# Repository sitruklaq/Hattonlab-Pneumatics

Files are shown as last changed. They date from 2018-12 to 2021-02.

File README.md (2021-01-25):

# 1. Overview
This system is designed to control multi-channel pneumatic smart surfaces using only small amounts of air. The pneumatic system consists of 8 independent pneumatic channels that can access positive, negative, and neutral (exhaust) states. For a smaller, portable setup, please refer to this respository: https://github.com/sitruklaq/Mini-Pneumatics

image of setup

topView backView

## 1.1 Table of Contents
* [1\. Overview](#1-overview)
  * [1\.1 Table of Contents](#11-table-of-contents)
* [2\. Components &amp; Pneumatic Logic](#2-components--pneumatic-logic)
* [3\. Instrument Control](#3-instrument-control)
  * [3\.1 Serial Command List](#31-serial-command-list)
    * [3\.1\.1 Valve Control](#311-valve-control)
    * [3\.1\.2 Reservoir Setpoints](#312-reservoir-setpoints)
    * [3\.1\.3 Pressure Readings](#313-pressure-readings)
* [4\. Visual Control App](#4-visual-control-app)
* [5\. Setpoint Pressure Control](#5-setpoint-pressure-control)
* [6\. Electrical Circuitry](#6-electrical-circuitry)
  * [6\.1 Electrical Components](#61-electrical-components)
  * [6\.2 PCBs](#62-pcbs)
    * [6\.2\.2 Input Valve PCB](#622-input-valve-pcb)
    * [6\.2\.3 Output Valve PCB](#623-output-valve-pcb)
    * [6\.2\.4 2 Sensor Board](#624-2-sensor-board)
[TOC]
# 2. Components & Pneumatic Logic

The instrument is designed to provide 3 pressure 'input' states: positive (+∆P), negative, (-∆P), and neutral (0∆P). Postive and negative pressures are generated through pneumatic pumps and held in reservoirs. The pressure for each reservoir is defined by the user and monitored through in-line pressure sensors. Pneumatic valves can be toggled to open and enter a common pressure line which can be accessed by independent valves that lead to channels (N=8). 

The valves are rated for +-100kPa while the pumps are generally able to reach ~+-60kPa. Valve response time is <5ms.

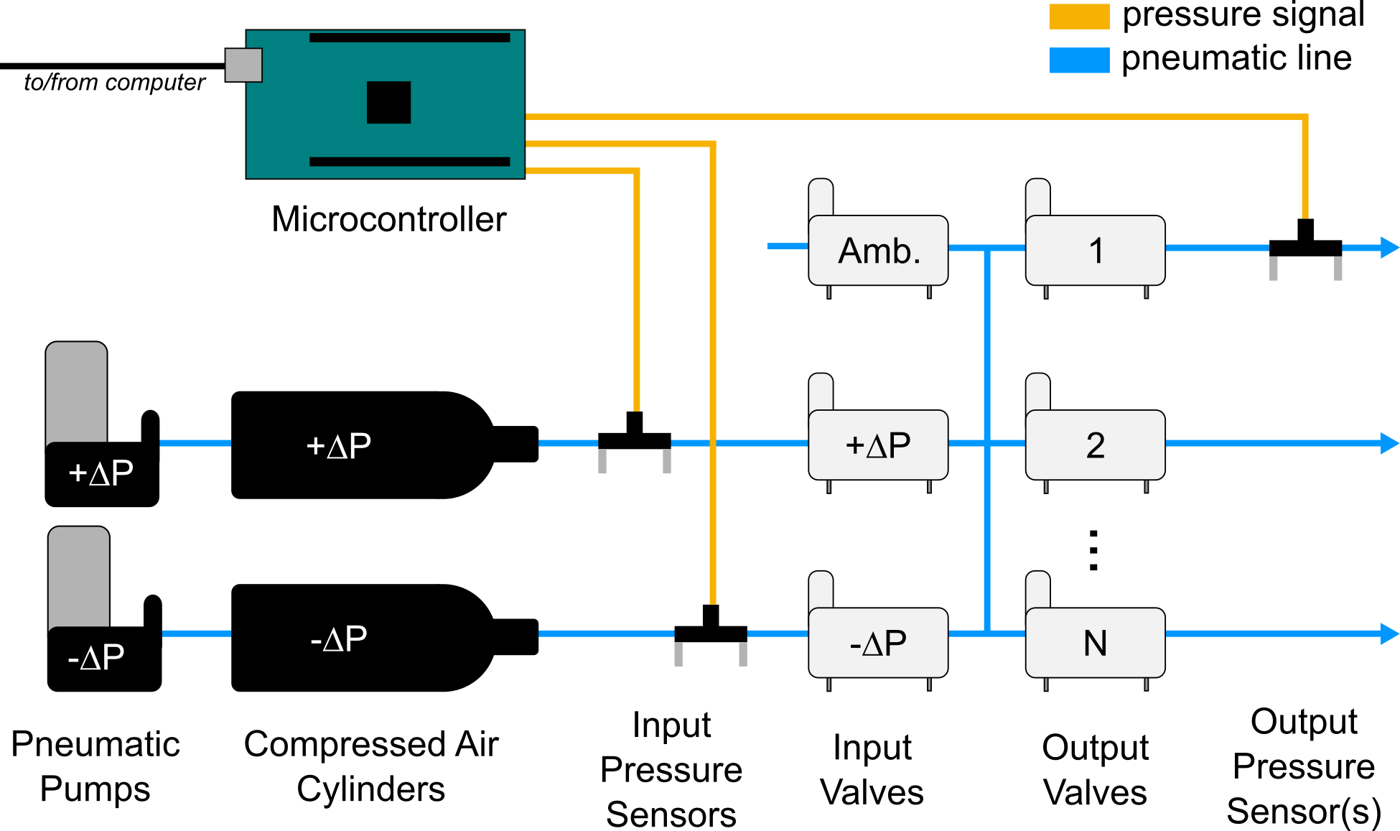
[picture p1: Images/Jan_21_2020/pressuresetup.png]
image of logic


# 3. Instrument Control

An Arduino microncontroller is responsible for opening and closing the pneumatic valves in addition to regulating pressure setpoints of the reservoirs. 

This instrument is controlled through a Serial Connection to a computer. 

Communication to the microcontroller is accomplished through serial communication. Commands for valve control, setpoint, and pressure value requests are available in the X section.

A MATLAB GUI app uses these commands to visually control the pneumatics.

screenshot to be added later.

## 3.1 Serial Command List

The Arduino is listening for serial commands in the following structure ‘< command, optional modifier, optional modifier>’.

### 3.1.1 Valve Control

| Command Syntax | Description                                                  | Example                                 |
| :------------: | ------------------------------------------------------------ | --------------------------------------- |
|     **VO**     | **VALVE OUTPUT** Changes the state of a single output valve. <command, valve # (0-7), valve state (0-closed 1-open)> | <VO, 4, 1> opens the fifth output valve |
|     **VI**     | **VALVE INPUT**Changes the state of a single input valve. <command, valve # (0-7), valve state (0-off 1-on)> | <VO, 4, 1> opens the fifth output valve |
|    **AIV**     | **ALL INPUT VALVES** Changes the state of all input valves <command, 0/1> | <AIV,1> opens all input valves          |
|    **AOV**     | **ALL OUTPUT VALVES** Changes the state of all outpu valves <command, 0/1> | <AOV, 0> turns off all output valves    |

### 3.1.2 Reservoir Setpoints

| Command Syntax | Description                                                  | Example    |
| :------------: | ------------------------------------------------------------ | ---------- |
|    **PSP**     | Changes setpoint of positive pressure reservoir              | <PSP, 15>  |
|    **NSP**     | Changes setpoint of negative pressure reservoir              | <NSP, -15> |
|    **PVN**     | **PRESSURE VALUE NEGATIVE** prints the pressure value of the negative pressure reservoir | <PVN>      |
|    **PVO**     | **PRESSURE VALUE OUTPUT** prints the pressure value of an output pressure channel | <PVO, 3>   |
|    **PVP**     | **PRESSURE VALUE POSITIVE** prints the pressure value of the positive pressure reservoir | <PVP>      |

### 3.1.3 Pressure Readings

| Command Syntax | Description                                                  | Example  |
| :------------: | ------------------------------------------------------------ | :------: |
|      PVP       | **PRESSURE VALUE POSITIVE** prints the pressure value of the positive pressure reservoir |  <PVP>   |
|      PVN       | **PRESSURE VALUE NEGATIVE** prints the pressure value of the negative pressure reservoir |  <PVN>   |
|      PVO       | **PRESSURE VALUE OUTPUT** prints the pressure value of an output pressure channel | <PVO, 3> |

# 4. Visual Control App

A visual control app was designed using Matlab App Designer. The app is basic in functionality but is able to control valves through sending serial commands. 

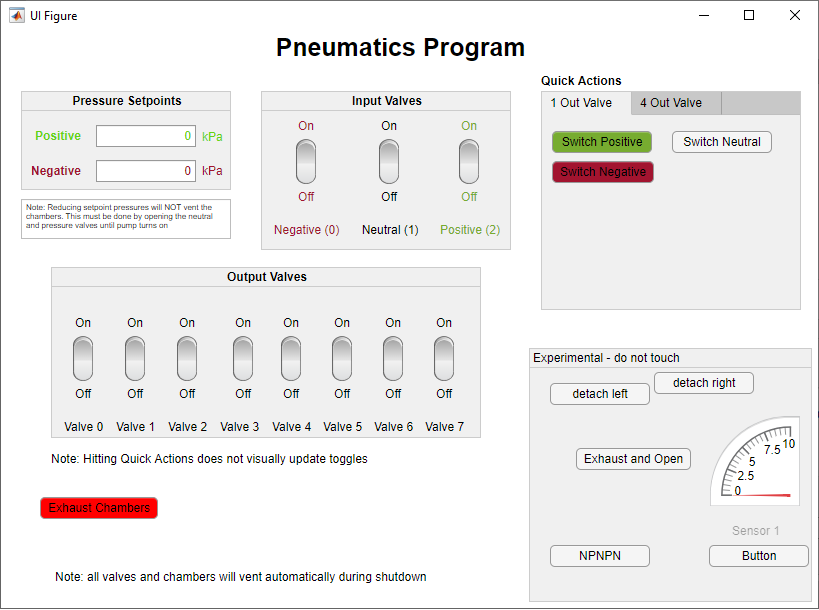
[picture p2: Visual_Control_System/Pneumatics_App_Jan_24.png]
VCA


# 5. Setpoint Pressure Control

Reservoir pressure is controlled by simple state monitoring. The pressure sensors monitor the pressure and the pump is turned on if the pressure drops below the Setpoint (with a small threshold).

# 6. Electrical Circuitry

## 6.1 Electrical Components

Power is supplied by an off board 12V 5A brick-style switching power supply. The 12V power is then split and one side is stepped down to 5V. The valves run on the 5V rail and are toggled through npn transistors powered by an Arduino.

**12V**

- Pumps
- Motor Controller

**5V**

- Valves

**5V (Computer-> Arduino)**

- pressure sensors
- transistors
- leds

## 6.2 PCBs

### 6.2.2 Input Valve PCB

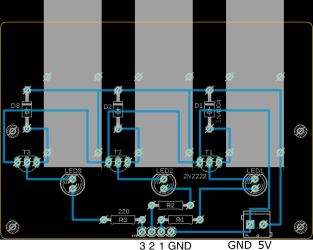
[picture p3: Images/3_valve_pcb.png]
3 valve pcb


### 6.2.3 Output Valve PCB

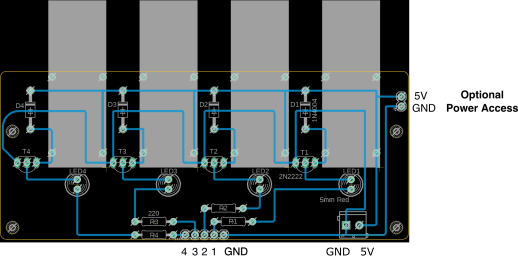
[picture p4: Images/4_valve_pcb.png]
4 valve pcb


### 6.2.4 2 Sensor Board

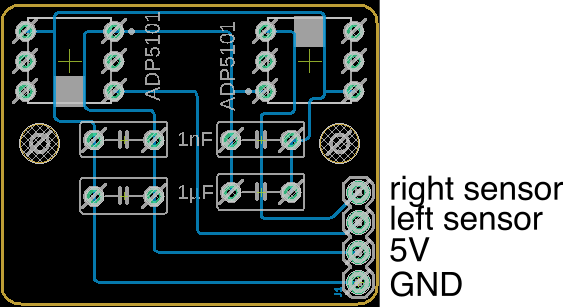
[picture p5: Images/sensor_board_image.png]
sensor board


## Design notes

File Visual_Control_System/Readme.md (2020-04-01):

# Things to Add

- [ ] Add pump pressure value gauges
- [ ] add pump power gauge
- [ ] add fluctuate quick action
- [ ] mimic valve positions to real device
- [ ] real-time update of toggle switches if quick actions are pressed

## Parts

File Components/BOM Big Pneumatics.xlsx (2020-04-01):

Hattonlab Pneumatics BOM
 | Description | Quantity | Unit Cost | Total Cost | Part Number` | Supplier | Purchase Link | Notes
Power Generation | Power Supply 12V 6A switching | 1 |  |  |  | creatroninc | not available
 | Barrel Jack 2.1mm DC | 1 | $0.65 | $0.65 |  | creatroninc | https://www.creatroninc.com/product/1mm-dc-barrel-jack/?search_query=barrel+jack&results=22
 | Switch SPST Rocker | 1 | $1.25 | $1.25 | SWROC-121801 | creatroninc | https://www.creatroninc.com/product/spst-rocker-switch/?search_query=switch&results=298
 | Voltage Regulator DROK DC Car Power Supply Voltage Regulator Buck Converter 8A/100W 12A Max DC 5-40V to 1.2-36V Step Down Volt Convert Module | 1 | $11.99 | $11.99 |  | amazon.ca | https://www.amazon.ca/gp/product/B00C4QVTNU/ref=ppx_yo_dt_b_search_asin_title?ie=UTF8&psc=1
Electrical Control | Arduino Mega Microcontroller | 1 | $19.99 | $19.99 | Arduino 2560 | amazon.ca | https://www.amazon.ca/Elegoo-Board-ATmega2560-ATMEGA16U2-Arduino/dp/B01H4ZDYCE?s=hi
 | Motor Controller L298 DUAL MOTOR DRIVER - 2A | 1 | $14.00 | $14.00 | PROMR-025298 | creatroninc | https://www.creatroninc.com/product/l298-dual-motor-driver-2a/?search_query=motor+controller&results=46 | I don’t think this is necessary and it is definitely a power hog.. Don’t use in version 2
Pneumatics | Pneumatic Pumps Vacuum Pump 12V Mini Diaphragm Air Compressor with Silicone Tube | 2 | $27.95 | $55.90 |  | creatroninc | https://www.creatroninc.com/product/12v-vacuum-pump/?search_query=pump&results=8
 | Pneumatic Valves | 11 | $6.95USD EA (min 25) | 76.45 |  | Jameco | https://www.jameco.com/z/RLB204KP30B-Asco-Valve-and-Instrument-2-Way-Barbed-Solenoid-Air-Valve-Normally-Closed_2258401.html | cheaper if purchased in bulk
Valve Control | terminal block
 | diode 1N4001 50V 1A rectifier Diode | 11 | 0.105 (0.42 per 4) | $1.16 | DIREC-004001 | creatroninc | https://www.creatroninc.com/product/1n4001-50v-1a-rectifier-diode-4-pack/?search_query=diode&results=75
 | transistor SS8050 - NPN BJT (25V 1.5A) | 11 | 0.6 | $6.60 | TRANQ-008050 | creatroninc | https://www.creatroninc.com/product/ss8050-npn-bjt-25v-15a/?search_query=transistor&results=146
 | resistor | 11 | ~0 | $0.00 |  | find a resistor pack around
 | led RED 5mm 2.2V 8mA | 11 | 0.1 (2.00 per 20) | $1.10 | LEDGE-000320 | creatroninc | https://www.creatroninc.com/product/3mm-led-red-20-pack/?search_query=led&results=464
sensor bank | pressure sensor Panasonic +-100kPa DIP mount | 7 | 60 | $420.00 | 769-ADP5101 | mouser.ca | https://www.mouser.ca/ProductDetail/Panasonic/ADP5101
 | capacitor
 | terminal block
PCBS | dual or one sided PCB | ~2 | $24 per 25 | 192% |  | bantamtools.com | https://www.bantamtools.com/miscellaneous/printed-circuit-board-blanks
Housing | Acrylic Sheet |  |  |  |  | mcmastercarr
 | standoffs |  |  |  |  | mcmastercarr
Assorted | tubing
 | luer connectors
 | check valves | 2 | 6.12CAD (per10) | 6.12 | Cole-Parmer AO-30505-92 | amazon.ca | https://www.amazon.ca/Cole-Parmer-One-way-silicone-diaphragm-female-male/dp/B003NVAG8O?s=gateway
 | standoffs and screws 250Pcs M3 Male to Female Hex Column Standoff Spacer Pillars Screws Nuts Assortment Kit with Storage Box (M3) | 1 pack | 18.69 |  |  | amazon.ca | https://www.amazon.ca/250Pcs-Standoff-Pillars-Assortment-Storage/dp/B071RXSMW6?s=gateway
 | electrical wiring

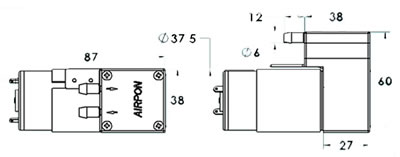
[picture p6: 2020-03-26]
Components/53cd24320585a-d2028bb.jpg

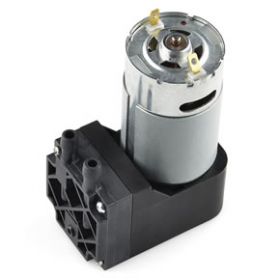
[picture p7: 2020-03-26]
Components/ROB-10398__00509.jpg

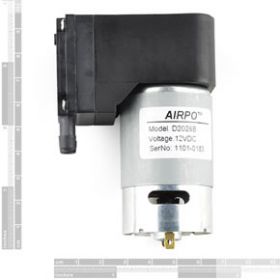
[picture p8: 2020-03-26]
Components/ROB-10398A__23939.jpg

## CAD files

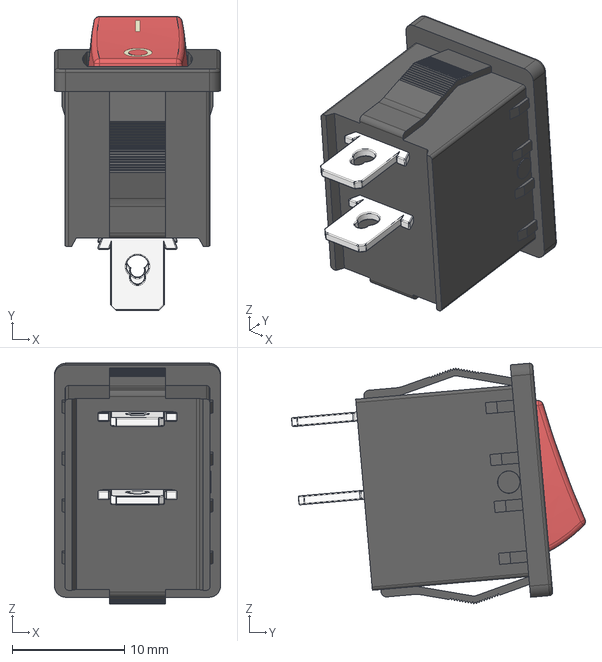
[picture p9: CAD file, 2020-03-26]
CAD FILES/rocker-switch-14/Rocker Assembly.stp
14.8 x 26.2 x 21.5 mm
Rocker SW samo taster horizont
Rocker SW samo telo

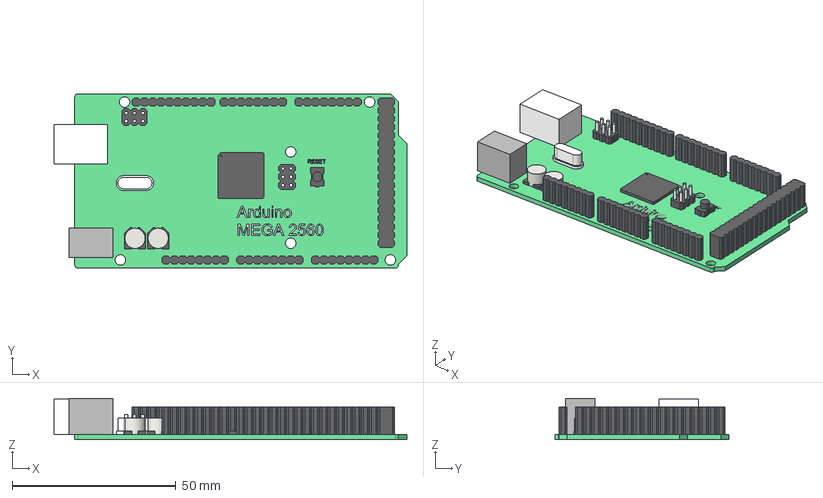
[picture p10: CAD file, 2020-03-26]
CAD FILES/arduino-mega-2560/ArduinoMEGA2560.stp
107.9 x 53.3 x 12.6 mm

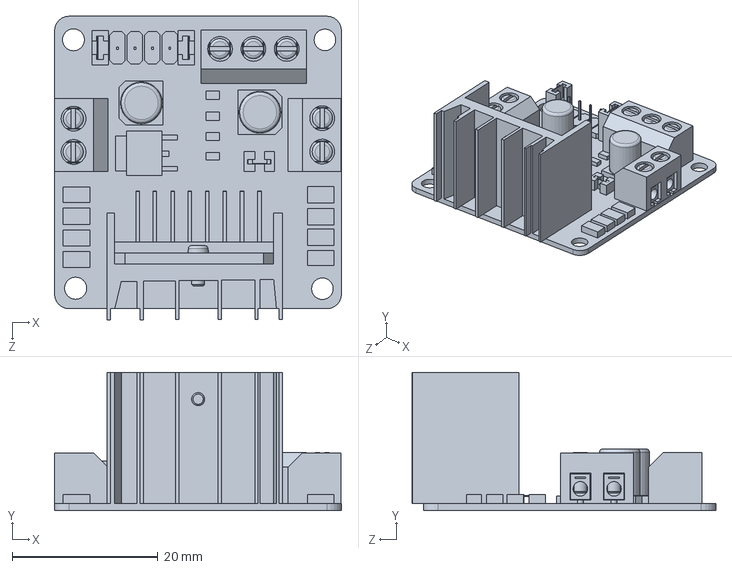
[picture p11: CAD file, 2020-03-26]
CAD FILES/l298n-driver-1/L298N Driver/L298N.SLDPRT
39.4 x 19.0 x 41.7 mm

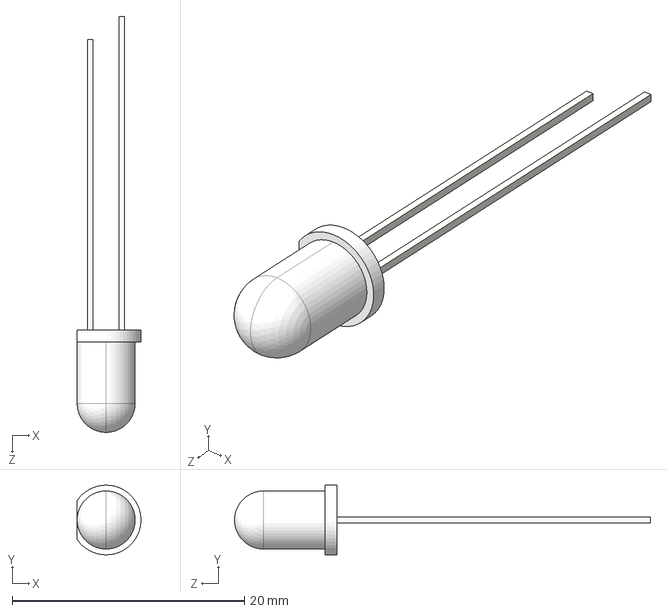
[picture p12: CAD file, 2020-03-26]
CAD FILES/led-5mm-1/LED 5mm.STEP
5.49 x 6.00 x 35.8 mm

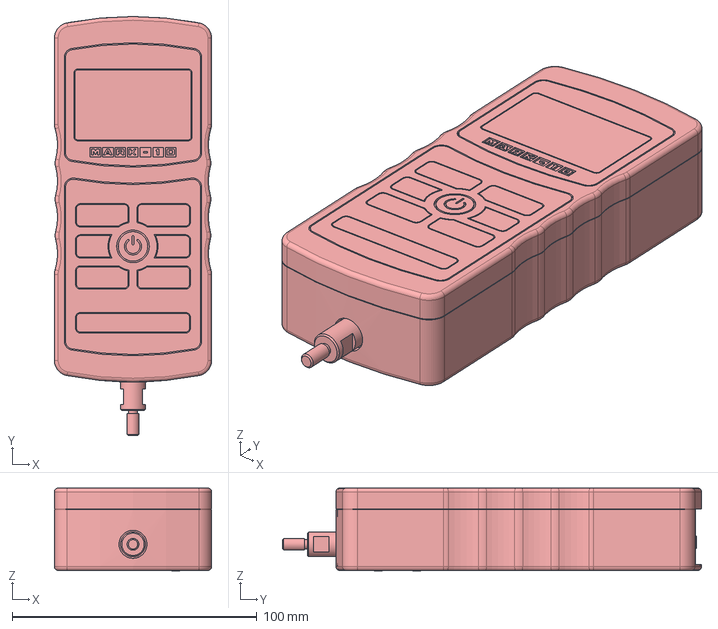
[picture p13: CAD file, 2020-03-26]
CAD FILES/M4/M4.stp
64.3 x 171.2 x 33.8 mm

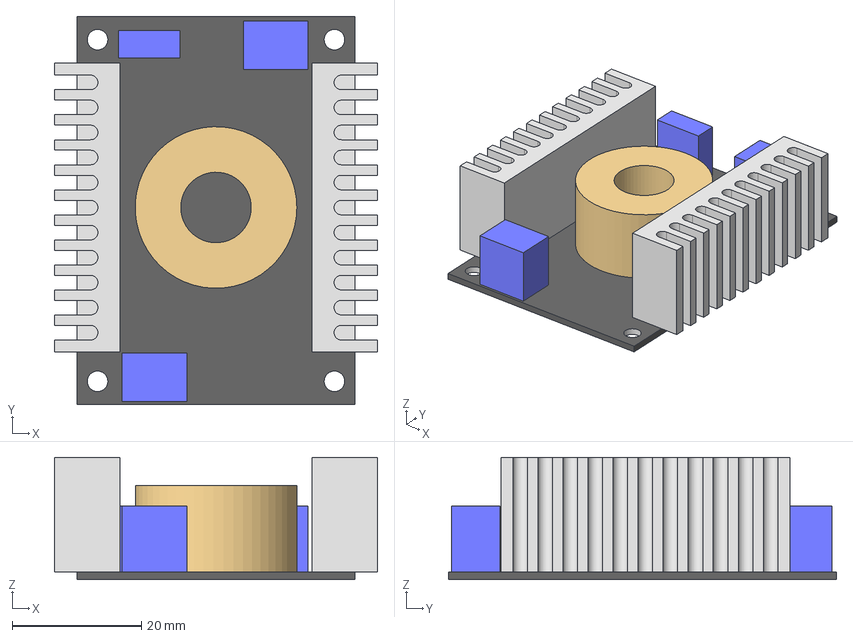
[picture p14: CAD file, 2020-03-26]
CAD FILES/Voltage Converter/DROK_090483.stp
50.0 x 60.0 x 18.9 mm

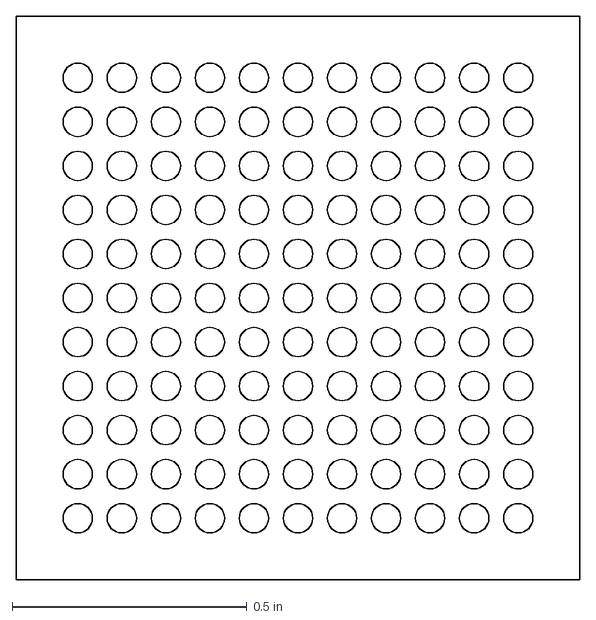
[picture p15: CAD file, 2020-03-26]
CAD FILES/holes.dxf
1.20 x 1.20 in

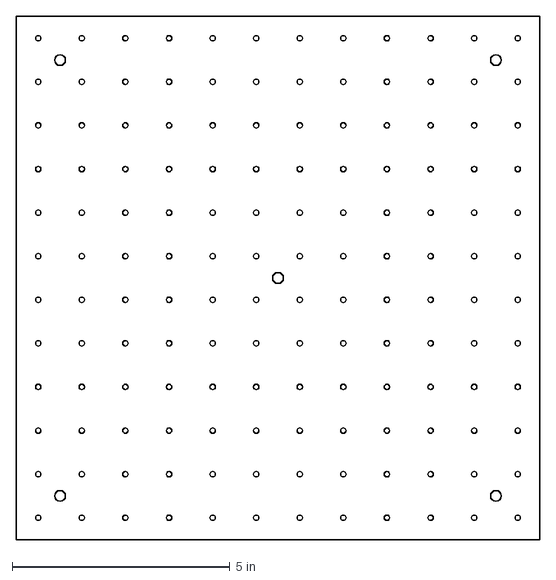
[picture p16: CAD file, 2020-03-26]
CAD FILES/top plate.dxf
12.0 x 12.0 in

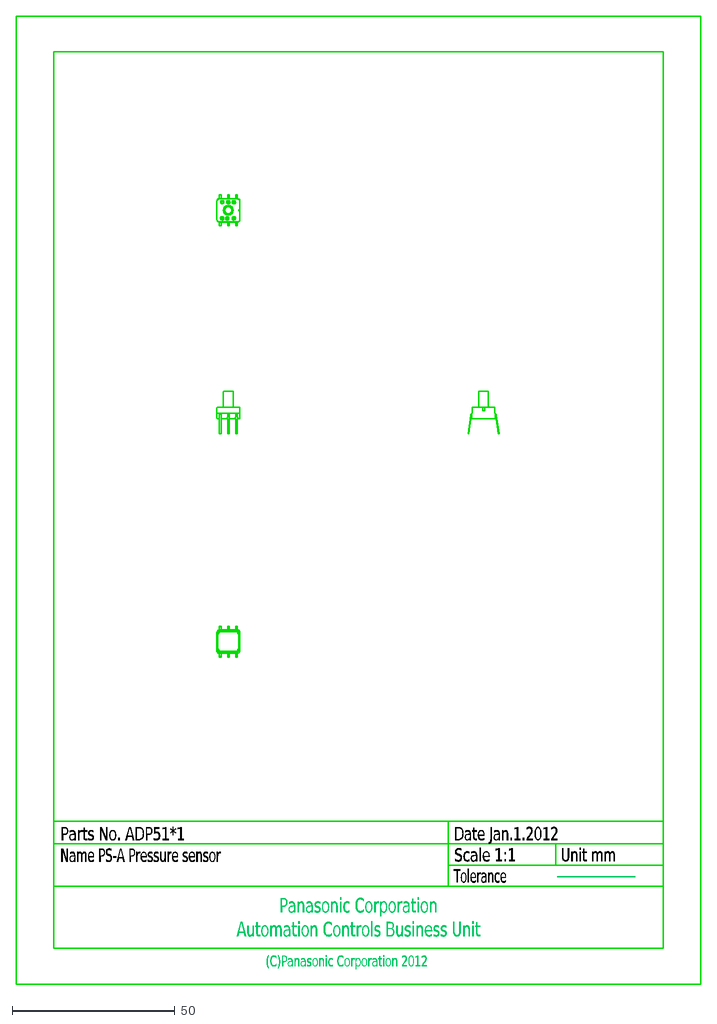
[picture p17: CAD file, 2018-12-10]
CAD FILES/adp5101.dxf
Parts No. ADP51*1
Name PS-A Pressure sensor
Scale 1:1
Unit mm
Tolerance
(C)Panasonic Corporation 2012
Panasonic Corporation Automation Controls Business Unit
Date Jan.1.2012

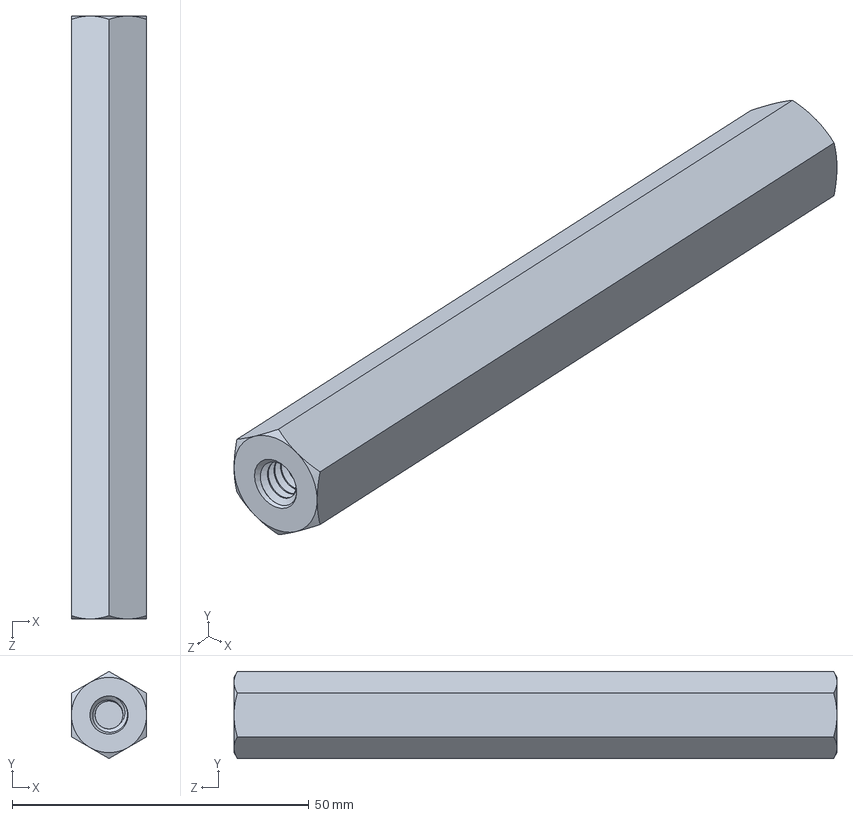
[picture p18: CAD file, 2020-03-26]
CAD FILES/91780A365_ALUM FEM THRDED HEX STANDOFF.SLDPRT
12.7 x 14.7 x 101.6 mm

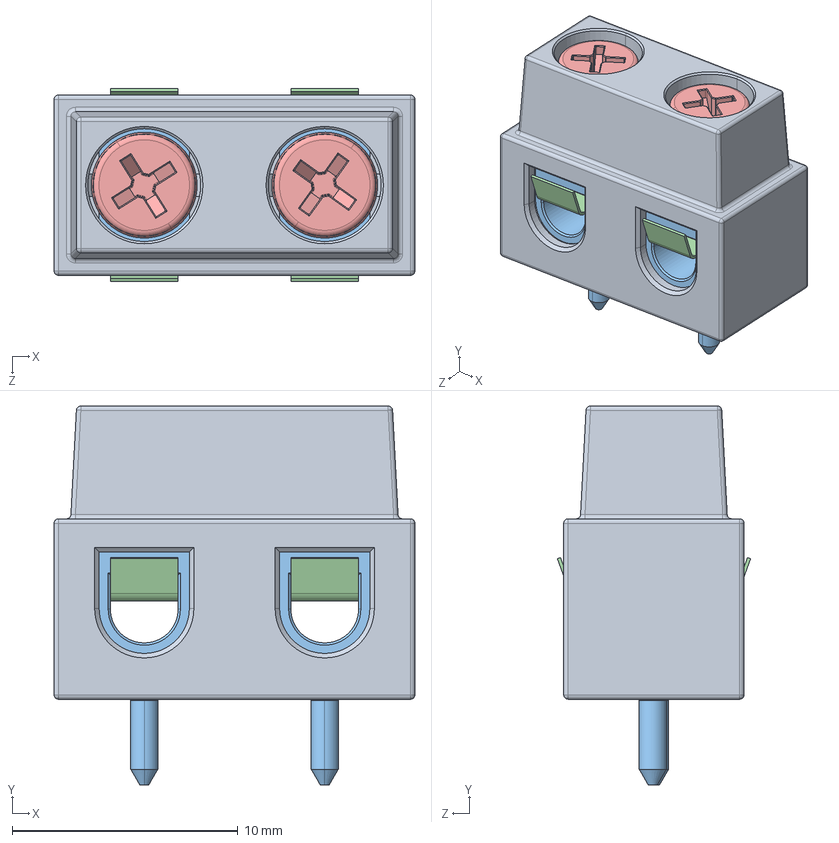
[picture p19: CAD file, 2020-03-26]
CAD FILES/screw-connection-terminal-1/Screw connection terminal.STEP
16.0 x 16.8 x 8.57 mm
terminal_S_case
wire insertion x 2
washer x 2
M2,5_0,35 x 2

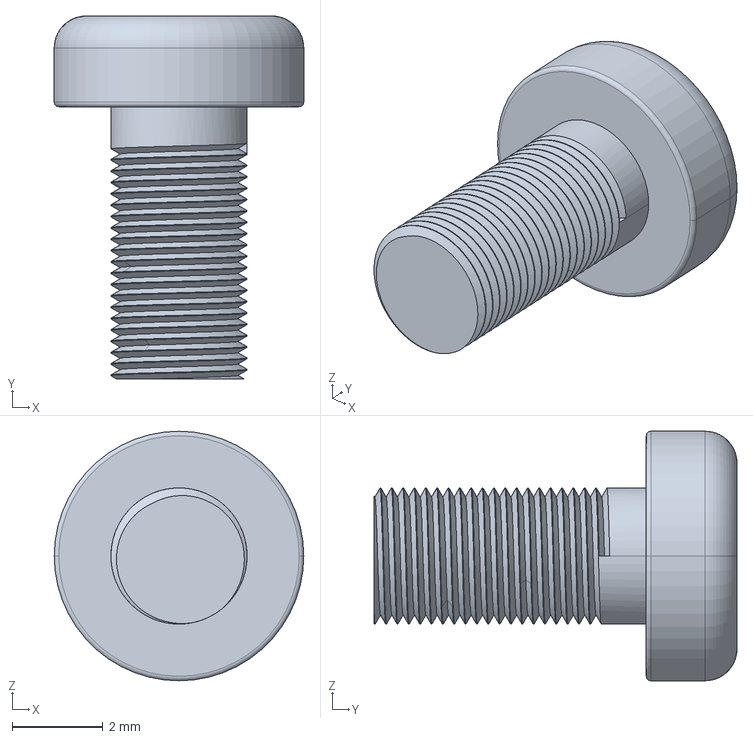
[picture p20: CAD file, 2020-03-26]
CAD FILES/screw-m3-x-0-5-length-6mm-pan-head-philips-drive-1/1220-1000-010-std-screw-m3x6.stp
5.50 x 8.00 x 5.50 mm

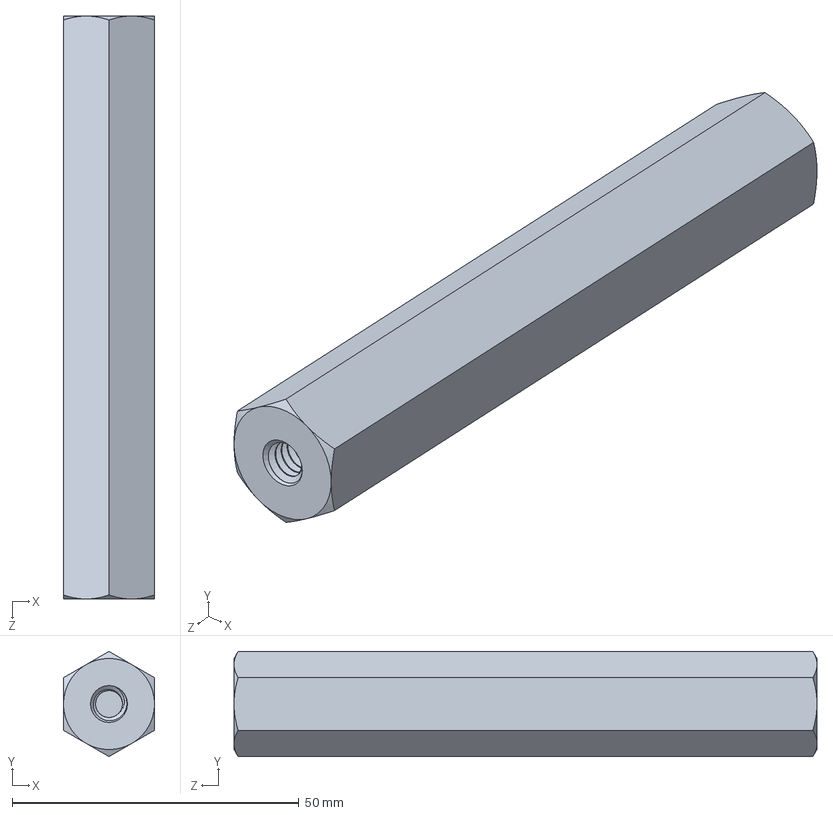
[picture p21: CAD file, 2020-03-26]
CAD FILES/91780A254_ALUM FEM THRDED HEX STANDOFF.SLDPRT
15.9 x 18.3 x 101.6 mm

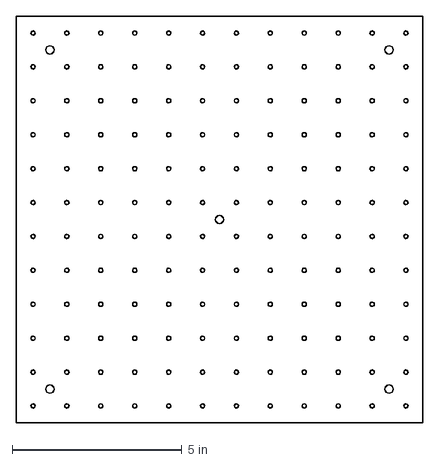
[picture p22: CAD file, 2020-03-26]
CAD FILES/screw-m3-x-0-5-length-6mm-pan-head-philips-drive-1/acrylic plates.dxf
12.0 x 12.0 in

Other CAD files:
CAD FILES/12v pump.f3d
CAD FILES/M4/M4.dwg
CAD FILES/M4/M4.igs
CAD FILES/Voltage Converter/DROK_090483.ipt
CAD FILES/air tank v1.f3d
CAD FILES/arduino-mega-2560/ArduinoMEGA2560.ipt
CAD FILES/arduino-mega-2560/ArduinoMega v1.f3d
CAD FILES/arduino-mega-2560/Arduino_MEGA2560.stl
CAD FILES/l298n-driver-1/L298N v1.f3d
CAD FILES/led-5mm-1/LED 5mm.IGS
CAD FILES/led-5mm-1/LED 5mm.SLDPRT
CAD FILES/led-5mm-1/LED 5mm.STL
CAD FILES/screw-m3-x-0-5-length-6mm-pan-head-philips-drive-1/1220-1000-010-std-screw-m3x6.igs

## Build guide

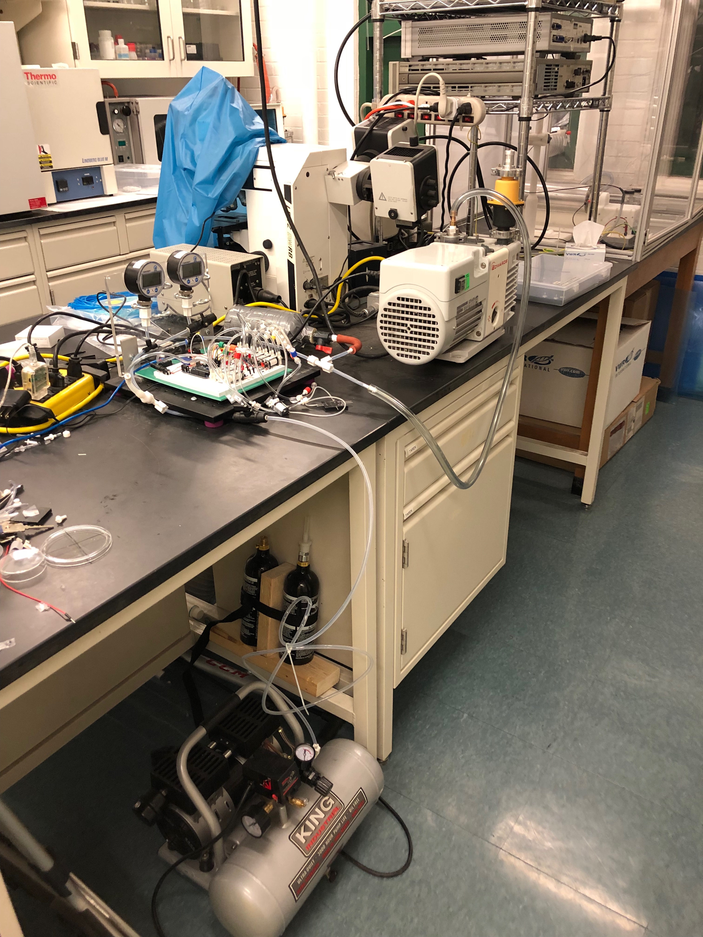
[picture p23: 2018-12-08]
Images/February 2018/Setup Feb 17 2018.jpg

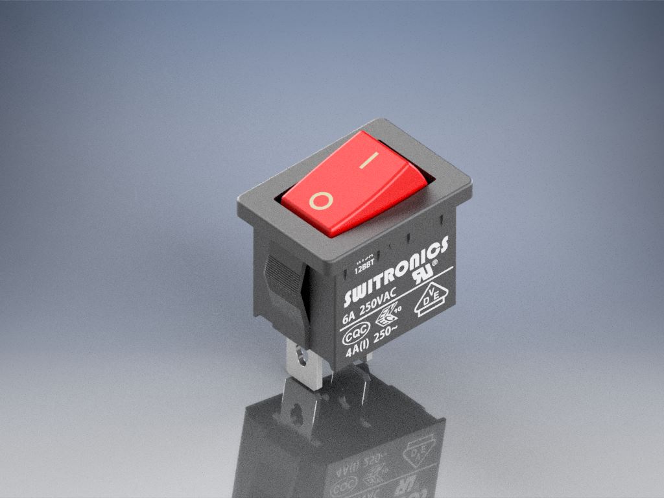
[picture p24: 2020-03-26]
CAD FILES/rocker-switch-14/Rocker Assembly.jpg

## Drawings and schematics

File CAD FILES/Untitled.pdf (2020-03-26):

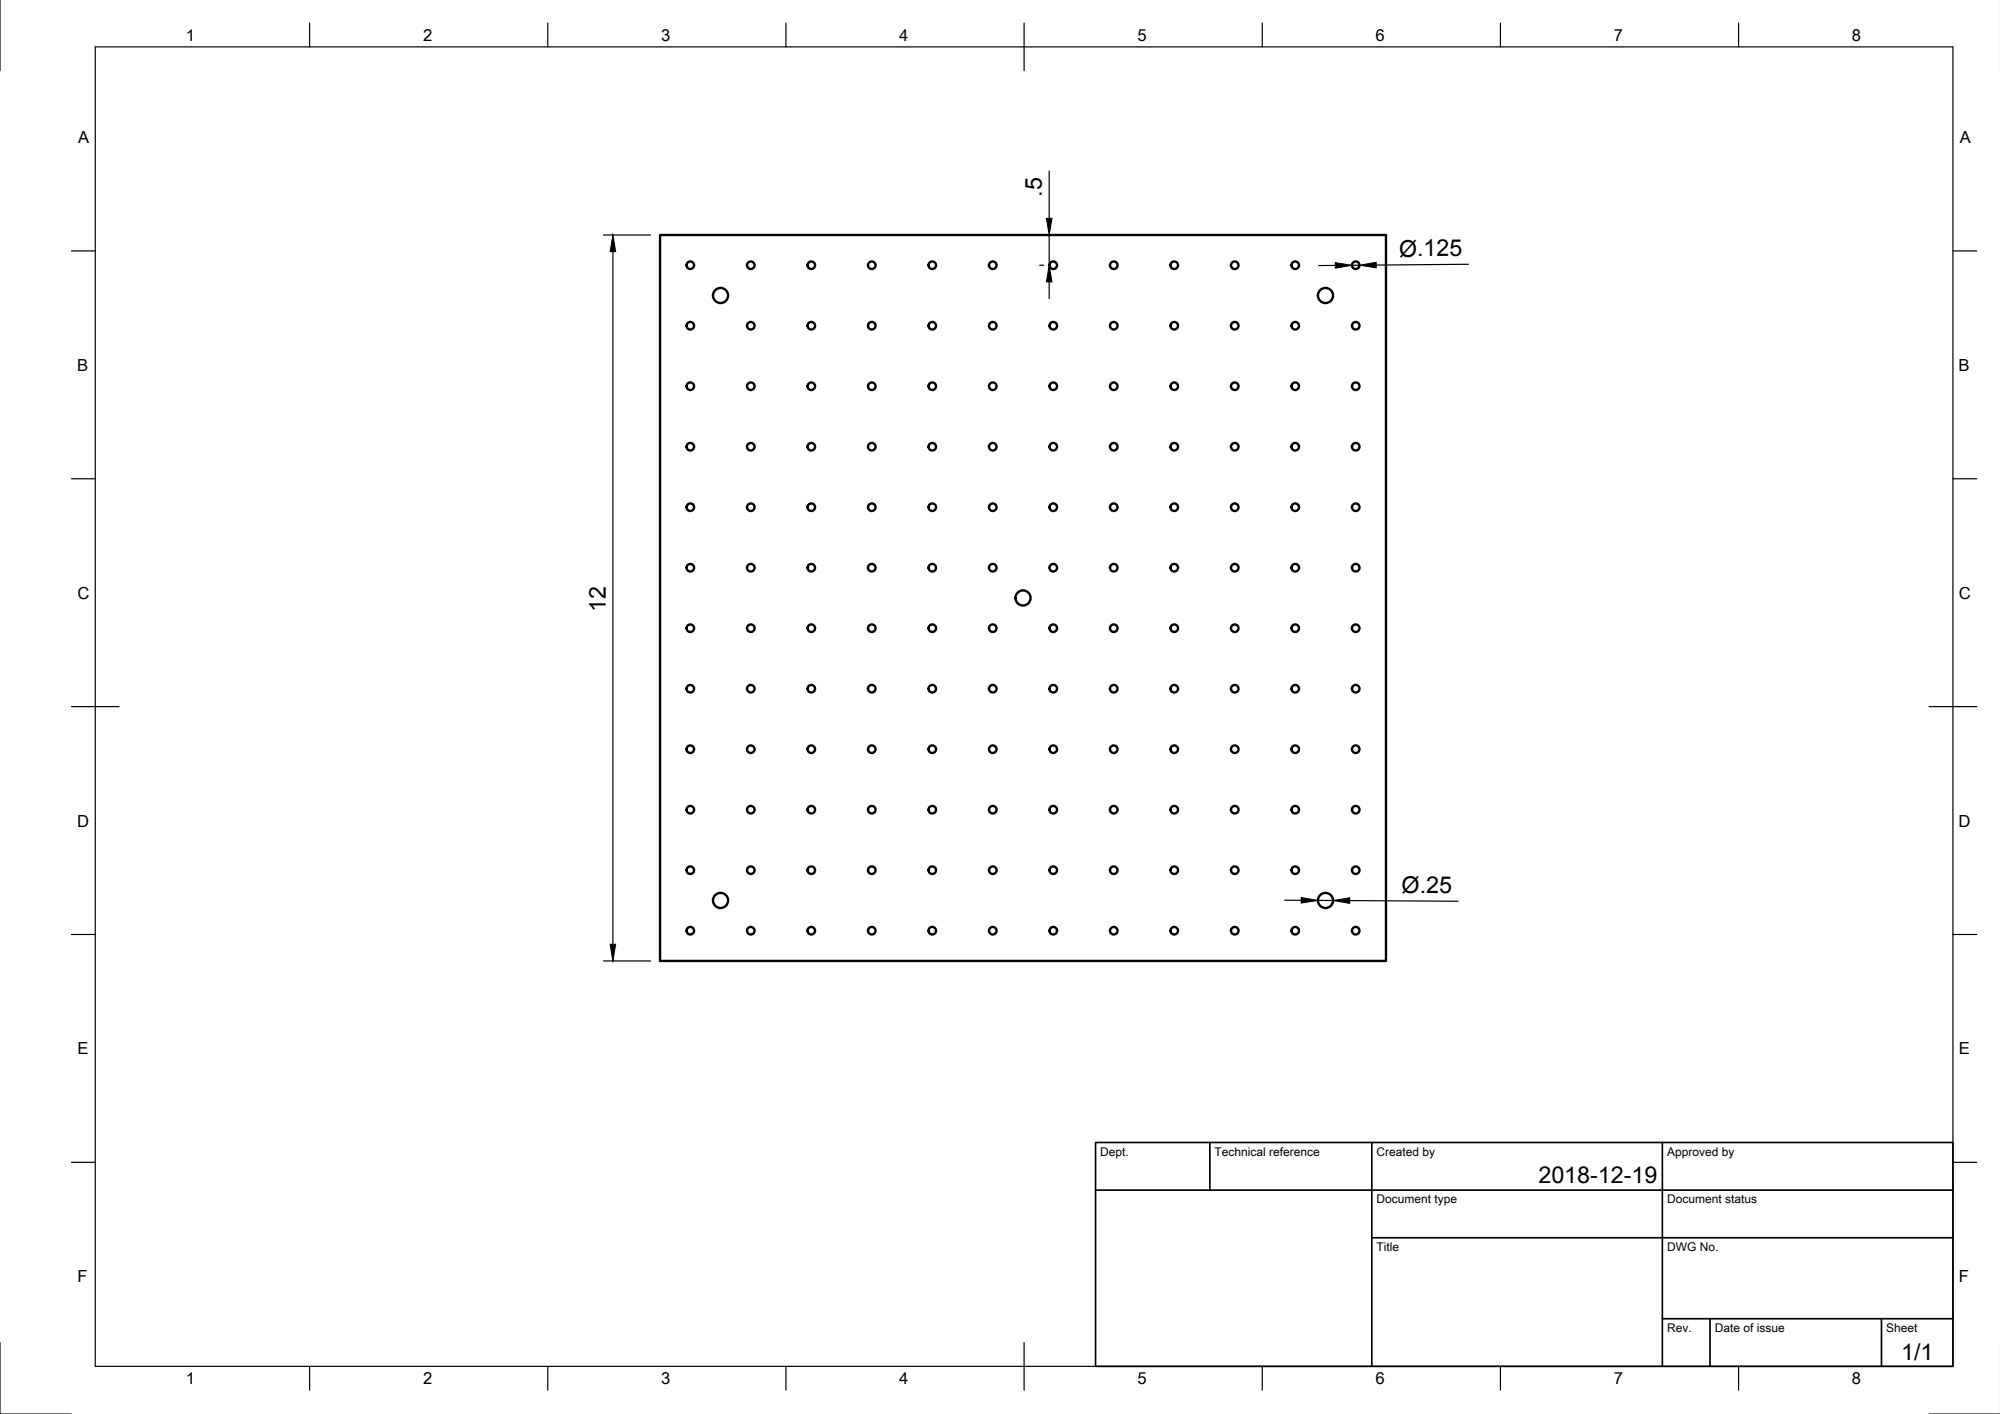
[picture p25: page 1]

Dept. | Technical reference | Created by 2018-12-19 | Approved by

Document type | Document status

Title | DWG No.

Rev. | Date of issue | Sheet 1/1

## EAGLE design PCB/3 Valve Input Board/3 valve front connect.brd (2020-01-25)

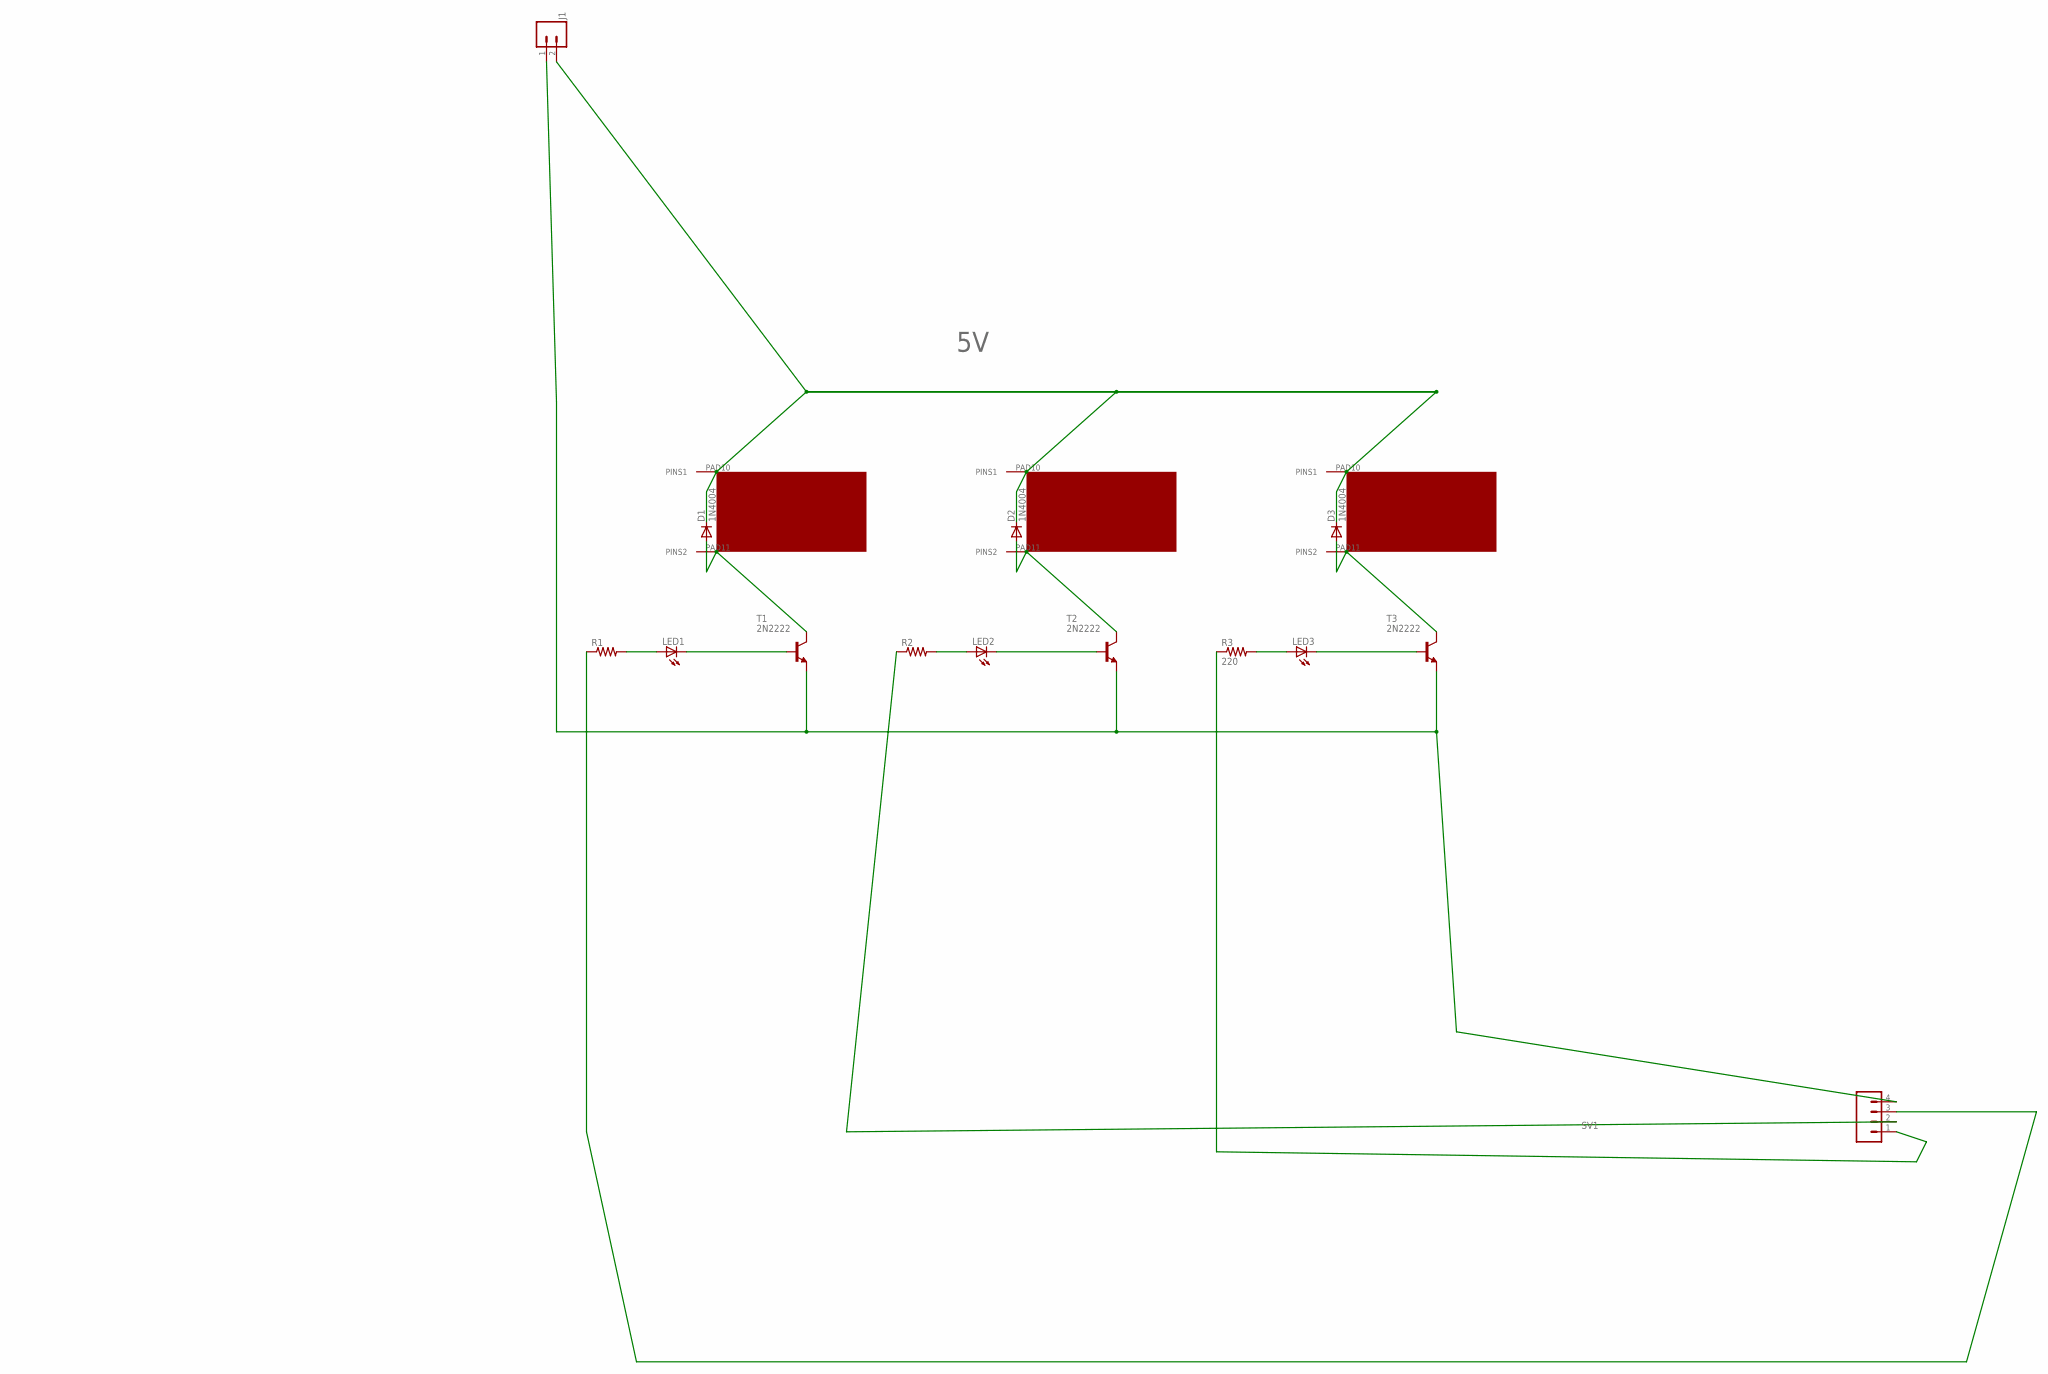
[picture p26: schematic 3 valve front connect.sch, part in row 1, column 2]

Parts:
D1, D2, D3: 1N4004; DO41-10
J1: CONN_023.5MM; SCREWTERMINAL-3.5MM-2
LED1, LED2, LED3: LED5MM
R1, R2: R-US_0207/10; 0207/10
R3: 220; 0207/10
SV1: CONN_04; 1X04
T1, T2, T3: 2N2222; TO92-EBC-OVAL
U$1, U$2: VALVE; VALVTEST2
VALVE3: VALVE; VALVTEST2

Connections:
5V: D1.C, D2.C, D3.C, J1.2, U$1.PAD10 (PINS1), U$2.PAD10 (PINS1), VALVE3.PAD10 (PINS1)
GND: J1.1, SV1.4, T1.E, T2.E, T3.E
unnamed: D1.A, T1.C, U$1.PAD11 (PINS2)
unnamed: LED1.K (C), T1.B
unnamed: LED1.A, R1.2
unnamed: D2.A, T2.C, U$2.PAD11 (PINS2)
unnamed: LED2.K (C), T2.B
unnamed: LED2.A, R2.2
unnamed: D3.A, T3.C, VALVE3.PAD11 (PINS2)
unnamed: LED3.K (C), T3.B
unnamed: LED3.A, R3.2
unnamed: R3.1, SV1.1
unnamed: R1.1, SV1.3
unnamed: R2.1, SV1.2

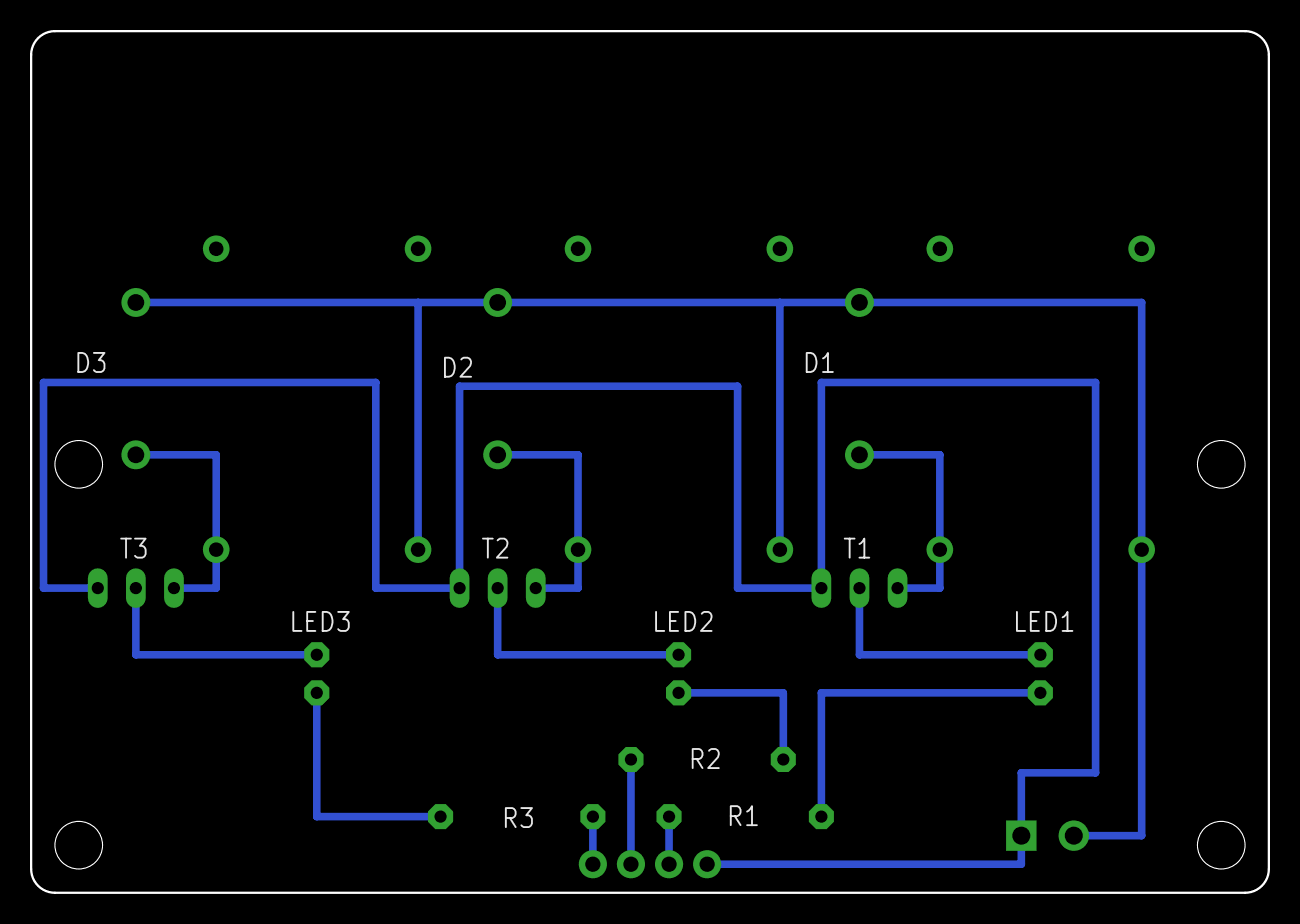
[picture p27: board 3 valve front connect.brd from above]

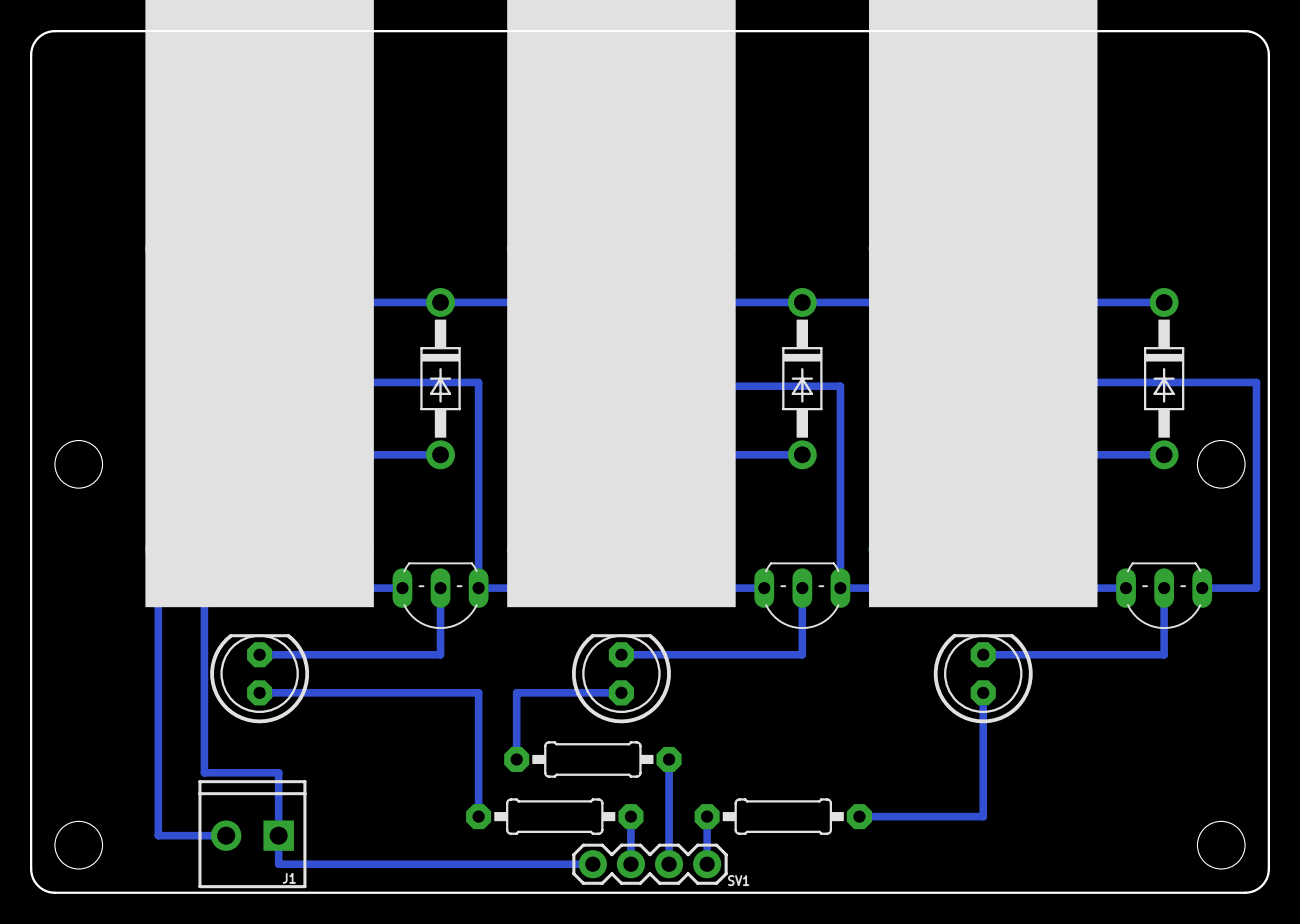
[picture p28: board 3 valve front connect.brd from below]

Board: 2 copper layers, 82.6 x 57.5 mm, 17 parts (17 on the bottom side), 14 nets.

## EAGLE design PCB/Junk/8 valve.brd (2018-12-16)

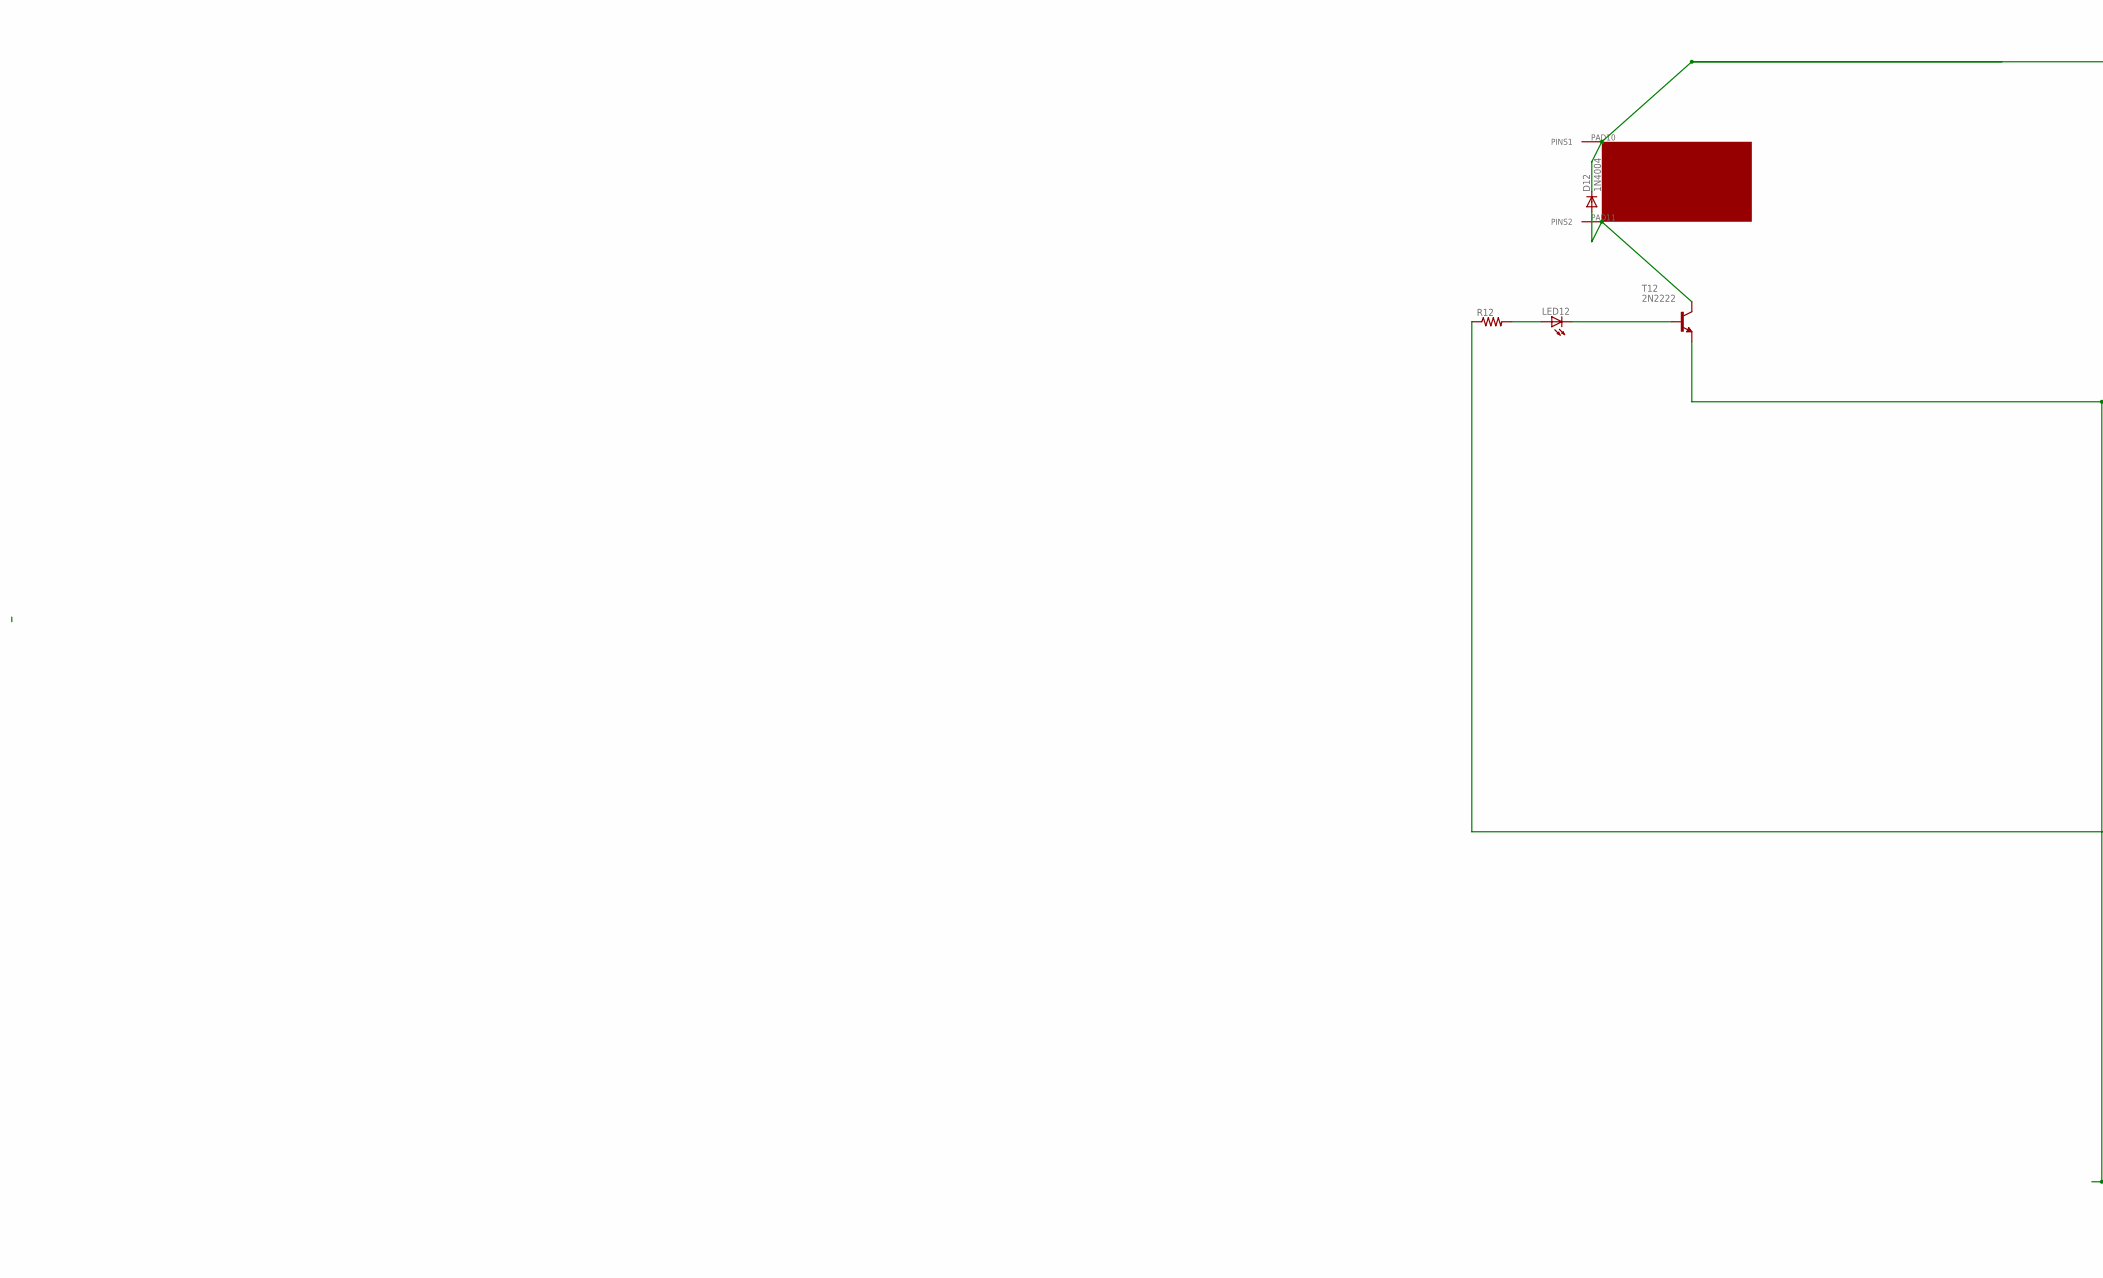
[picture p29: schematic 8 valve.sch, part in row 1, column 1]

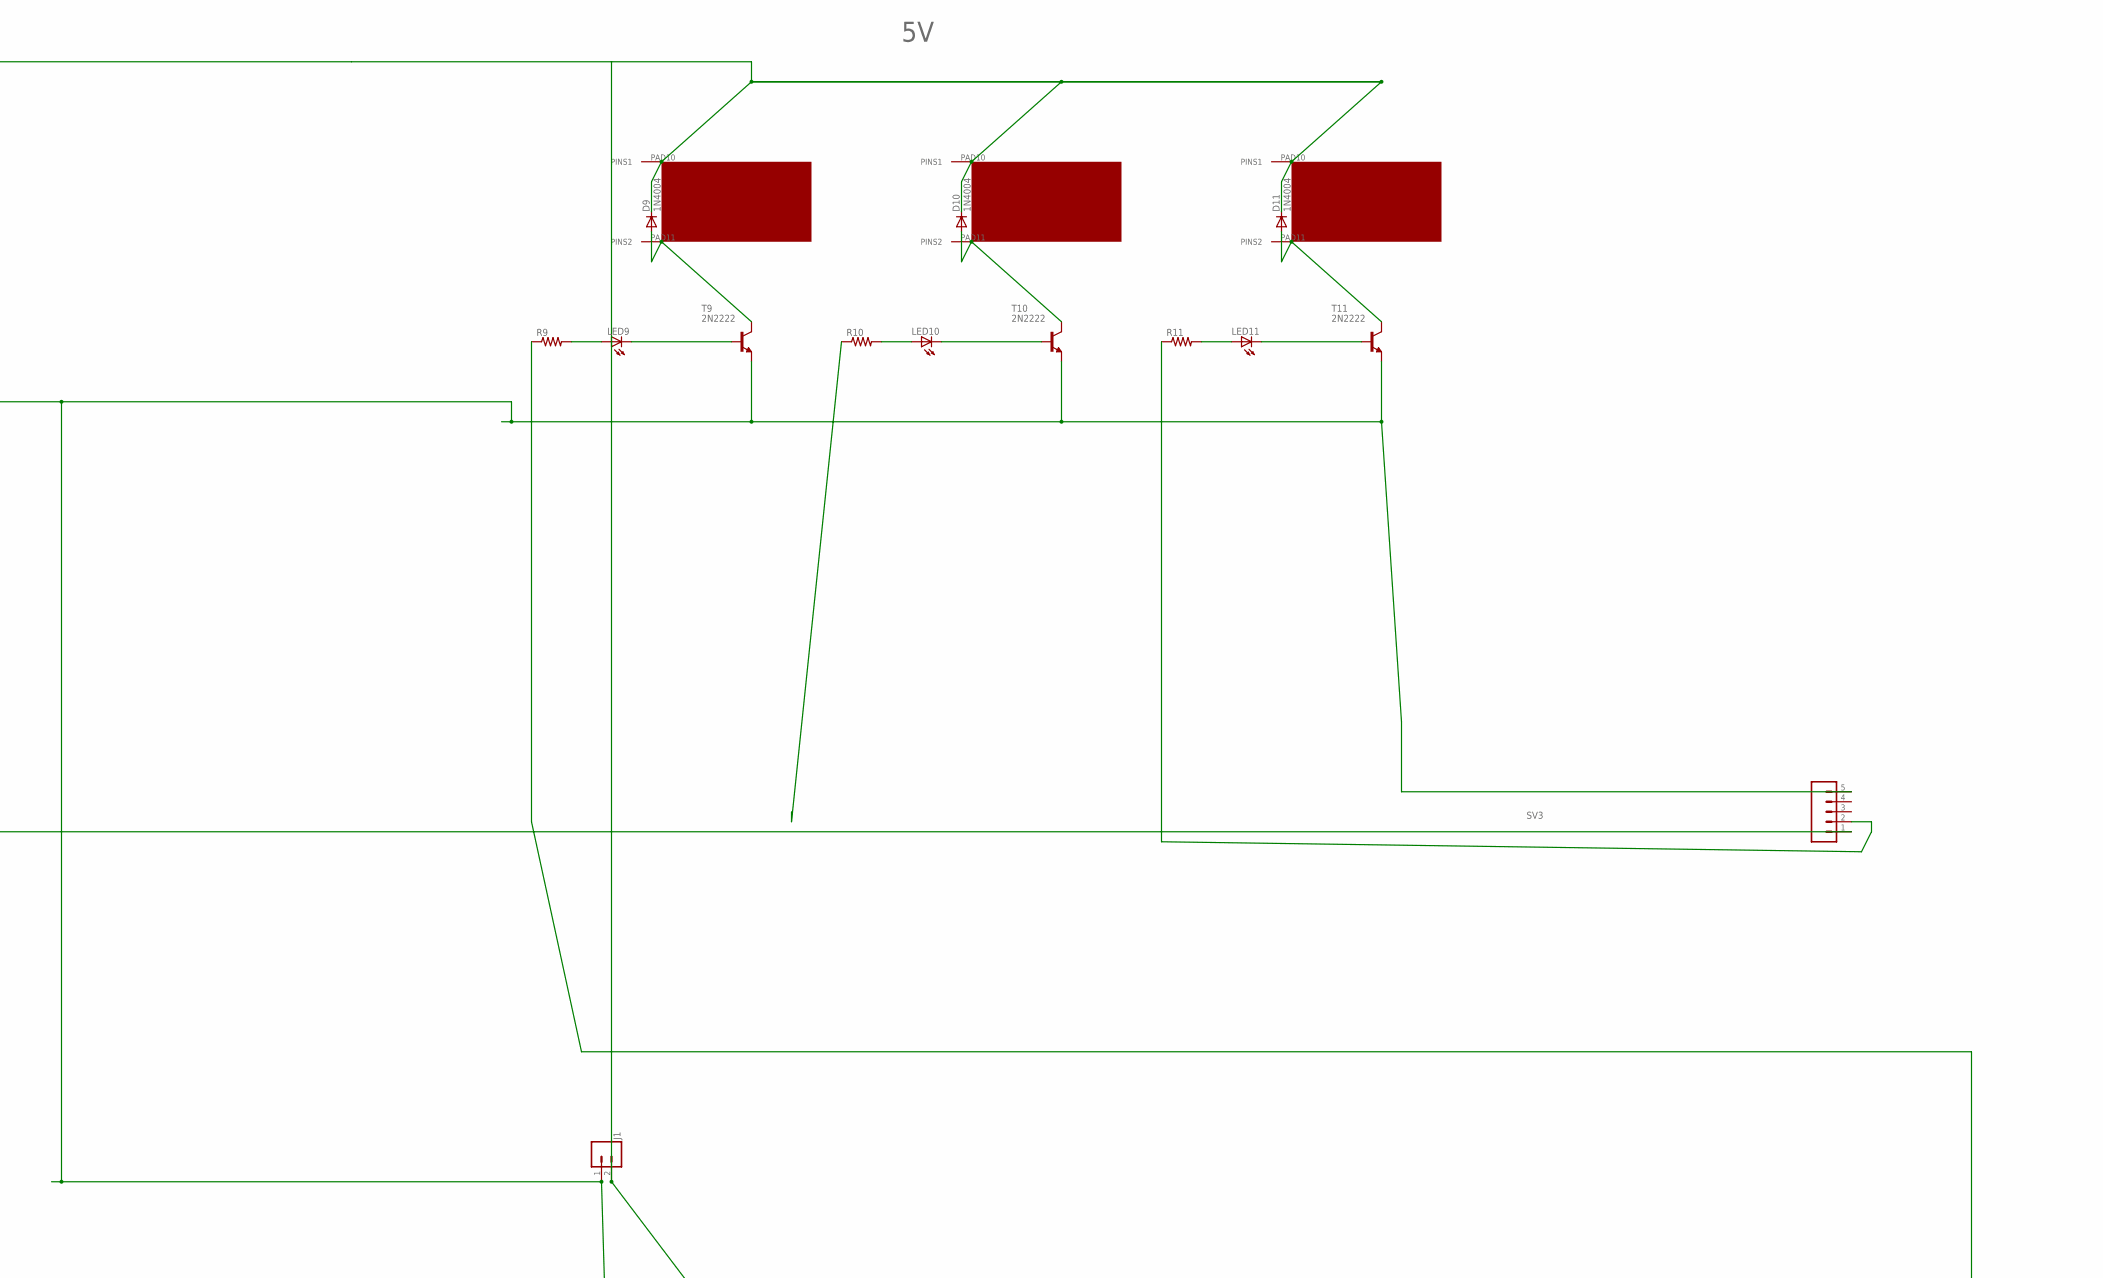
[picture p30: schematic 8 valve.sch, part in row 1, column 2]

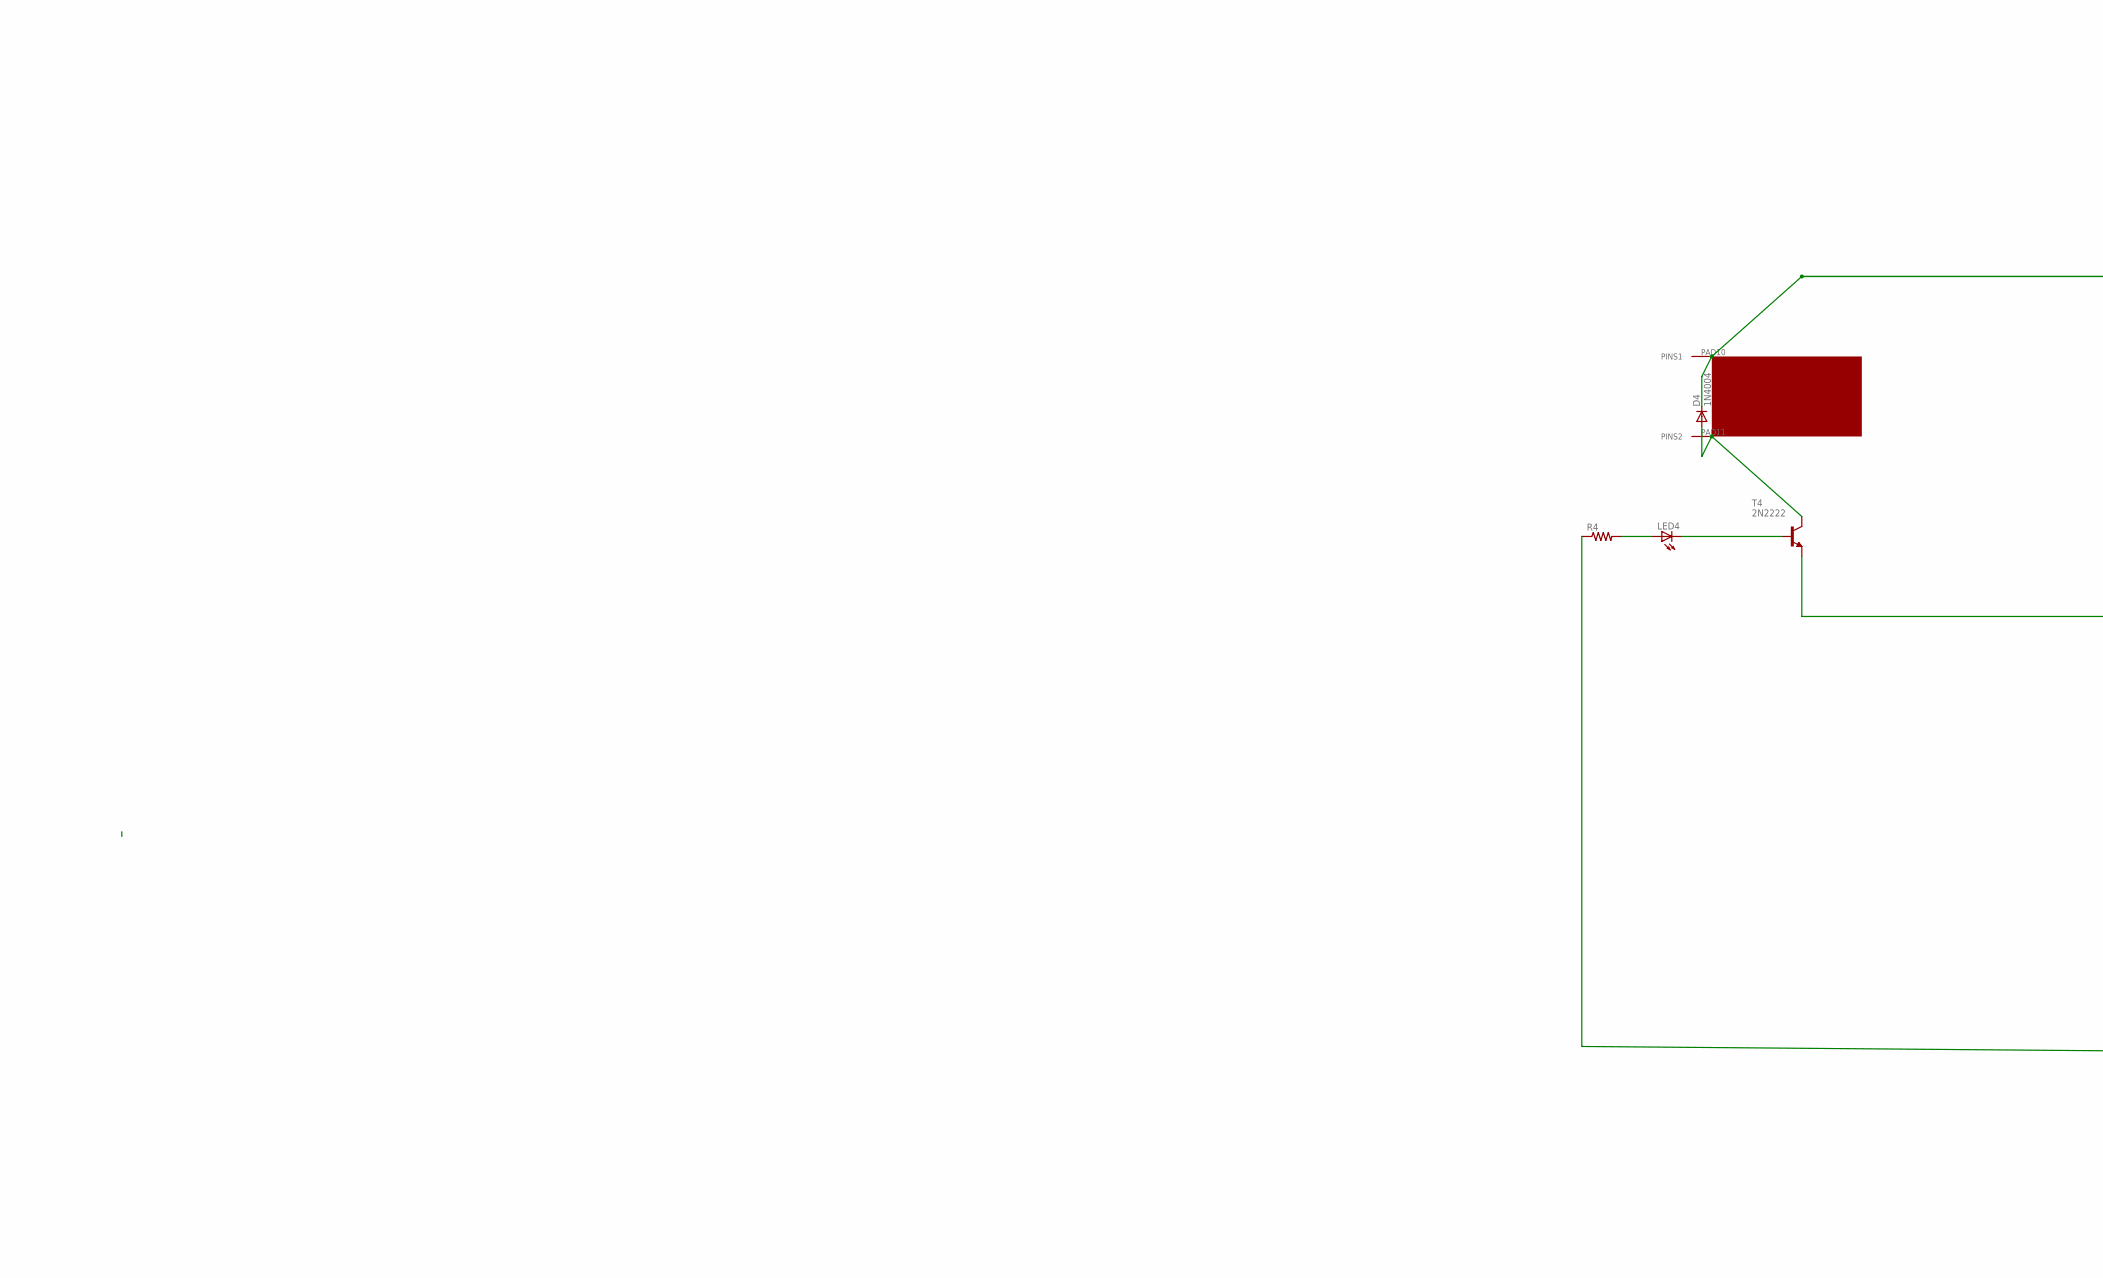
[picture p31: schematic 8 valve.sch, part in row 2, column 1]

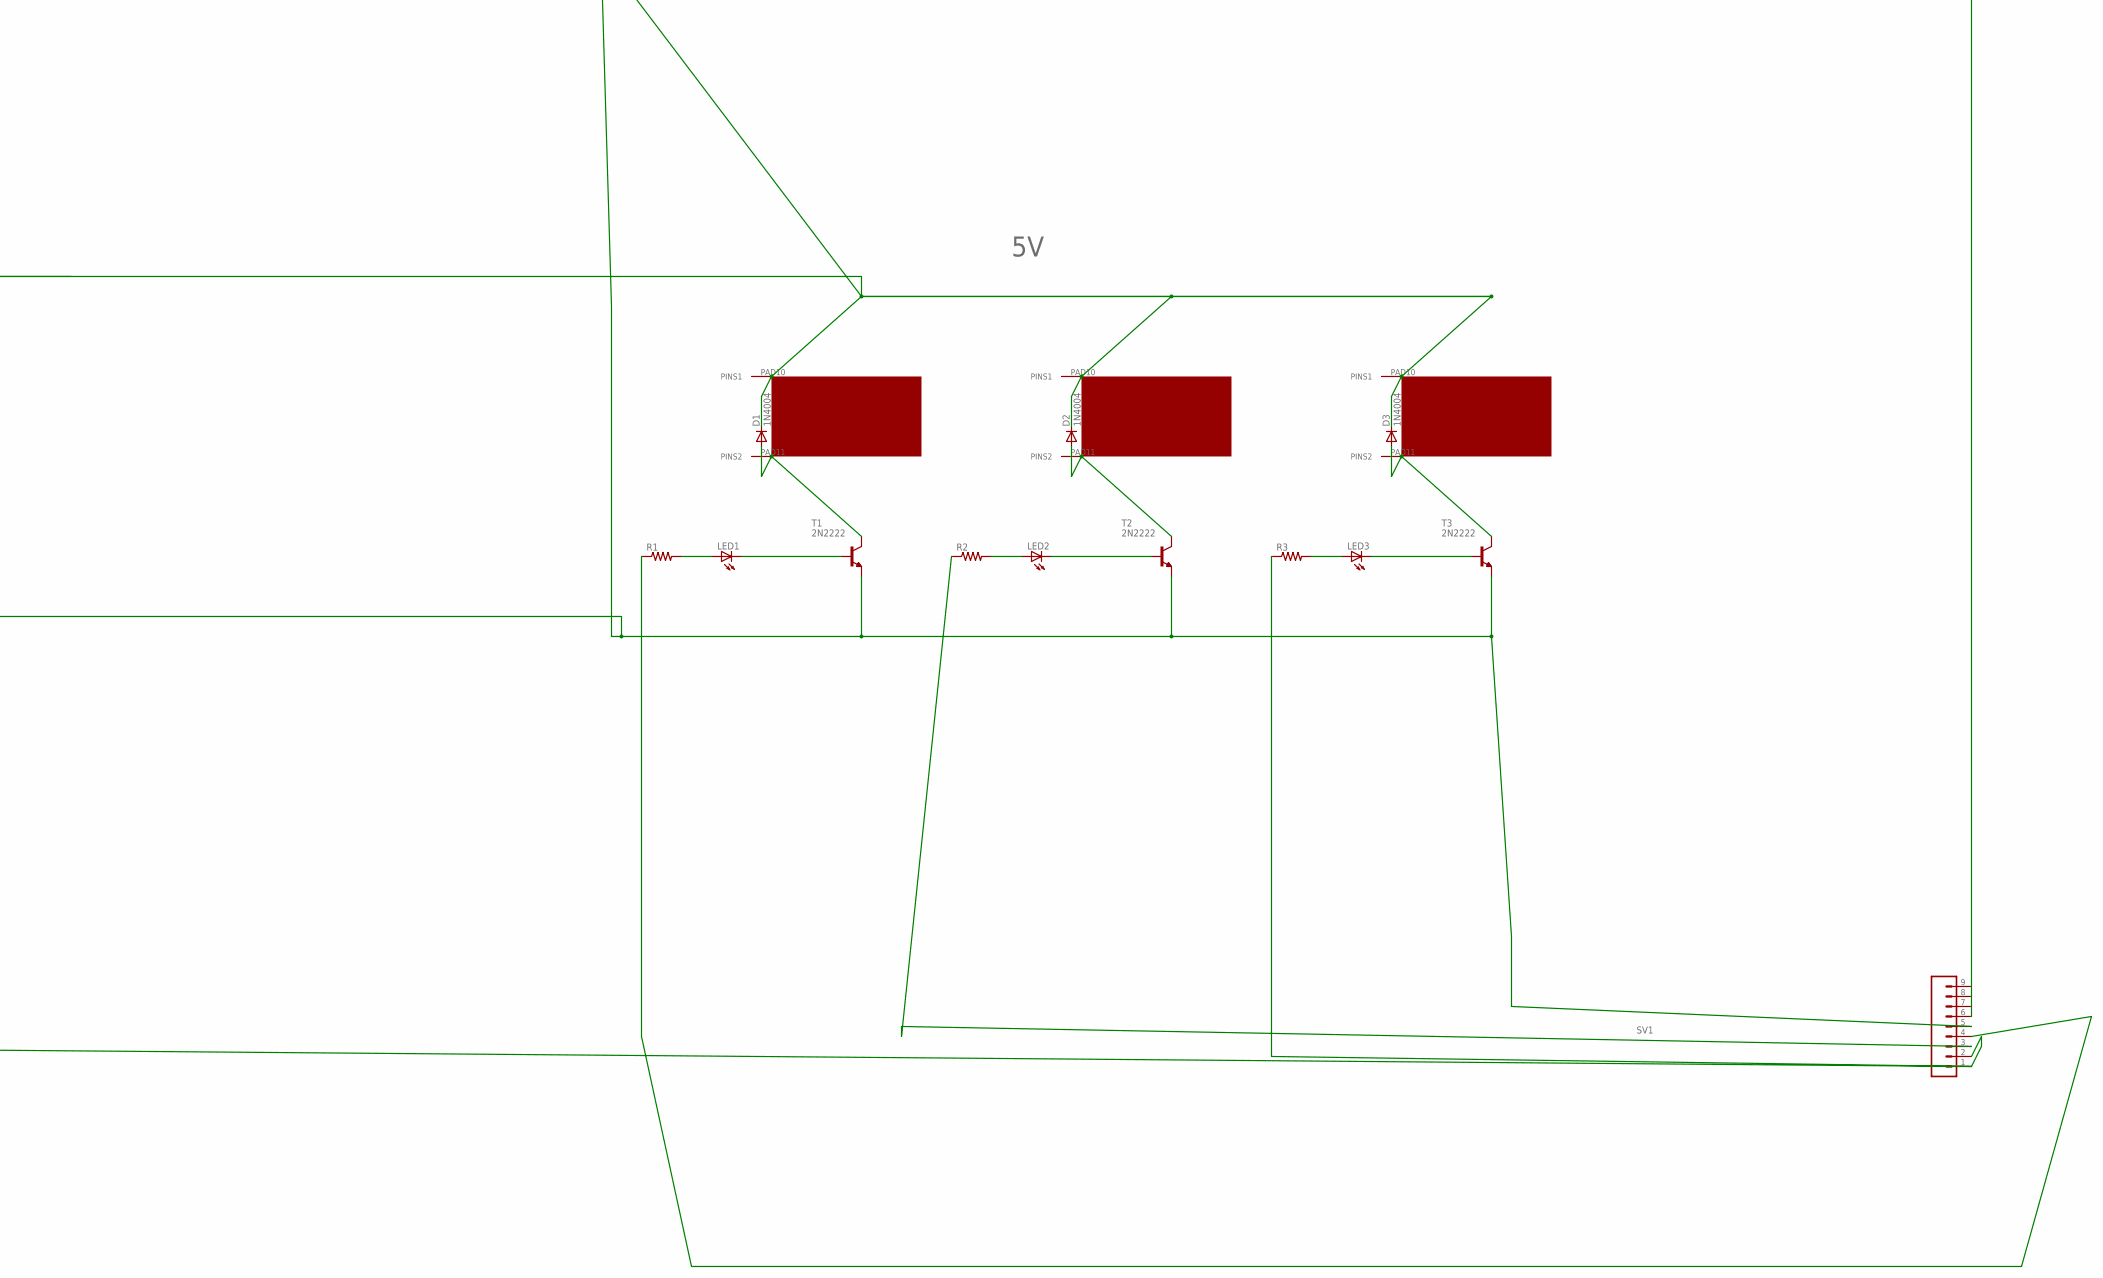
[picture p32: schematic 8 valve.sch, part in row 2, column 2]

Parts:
D1, D2, D3, D4, D9, D10, D11, D12: 1N4004; DO41-10
J1: CONN_023.5MM; SCREWTERMINAL-3.5MM-2
LED1, LED2, LED3, LED4, LED9, LED10, LED11, LED12: LED5MM
R1, R2, R3, R4, R9, R10, R11, R12: R-US_0207/10; 0207/10
SV1: CONN_09; 1X09
SV3: CONN_05; 1X05
T1, T2, T3, T4, T9, T10, T11, T12: 2N2222; TO92-EBC-OVAL
U$1, U$2, U$3, U$7, U$8, U$9: VALVE; VALVTEST2
VALVE2, VALVE3: VALVE; VALVTEST2

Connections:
5V: D1.C, D2.C, D3.C, D4.C, D9.C, D10.C, D11.C, D12.C, J1.2, U$1.PAD10 (PINS1), U$2.PAD10 (PINS1), U$3.PAD10 (PINS1), U$7.PAD10 (PINS1), U$8.PAD10 (PINS1), U$9.PAD10 (PINS1), VALVE2.PAD10 (PINS1), VALVE3.PAD10 (PINS1)
GND: J1.1, SV1.5, SV3.5, T1.E, T2.E, T3.E, T4.E, T9.E, T10.E, T11.E, T12.E
unnamed: D1.A, T1.C, U$1.PAD11 (PINS2)
unnamed: LED1.K (C), T1.B
unnamed: LED1.A, R1.2
unnamed: D4.A, T4.C, U$3.PAD11 (PINS2)
unnamed: D2.A, T2.C, U$2.PAD11 (PINS2)
unnamed: LED2.K (C), T2.B
unnamed: LED2.A, R2.2
unnamed: LED4.K (C), T4.B
unnamed: D3.A, T3.C, VALVE3.PAD11 (PINS2)
unnamed: LED3.K (C), T3.B
unnamed: LED3.A, R3.2
unnamed: LED4.A, R4.2
unnamed: R4.1, SV1.1
unnamed: R2.1, SV1.3
unnamed: R12.1, SV3.1
unnamed: R3.1, SV1.2
unnamed: R9.1, SV1.6
unnamed: R1.1, SV1.4
unnamed: D9.A, T9.C, U$7.PAD11 (PINS2)
unnamed: LED9.K (C), T9.B
unnamed: LED9.A, R9.2
unnamed: D10.A, T10.C, U$8.PAD11 (PINS2)
unnamed: LED10.K (C), T10.B
unnamed: LED10.A, R10.2
unnamed: D11.A, T11.C, VALVE2.PAD11 (PINS2)
unnamed: LED11.K (C), T11.B
unnamed: LED11.A, R11.2
unnamed: R11.1, SV3.2
unnamed: D12.A, T12.C, U$9.PAD11 (PINS2)
unnamed: LED12.K (C), T12.B
unnamed: LED12.A, R12.2

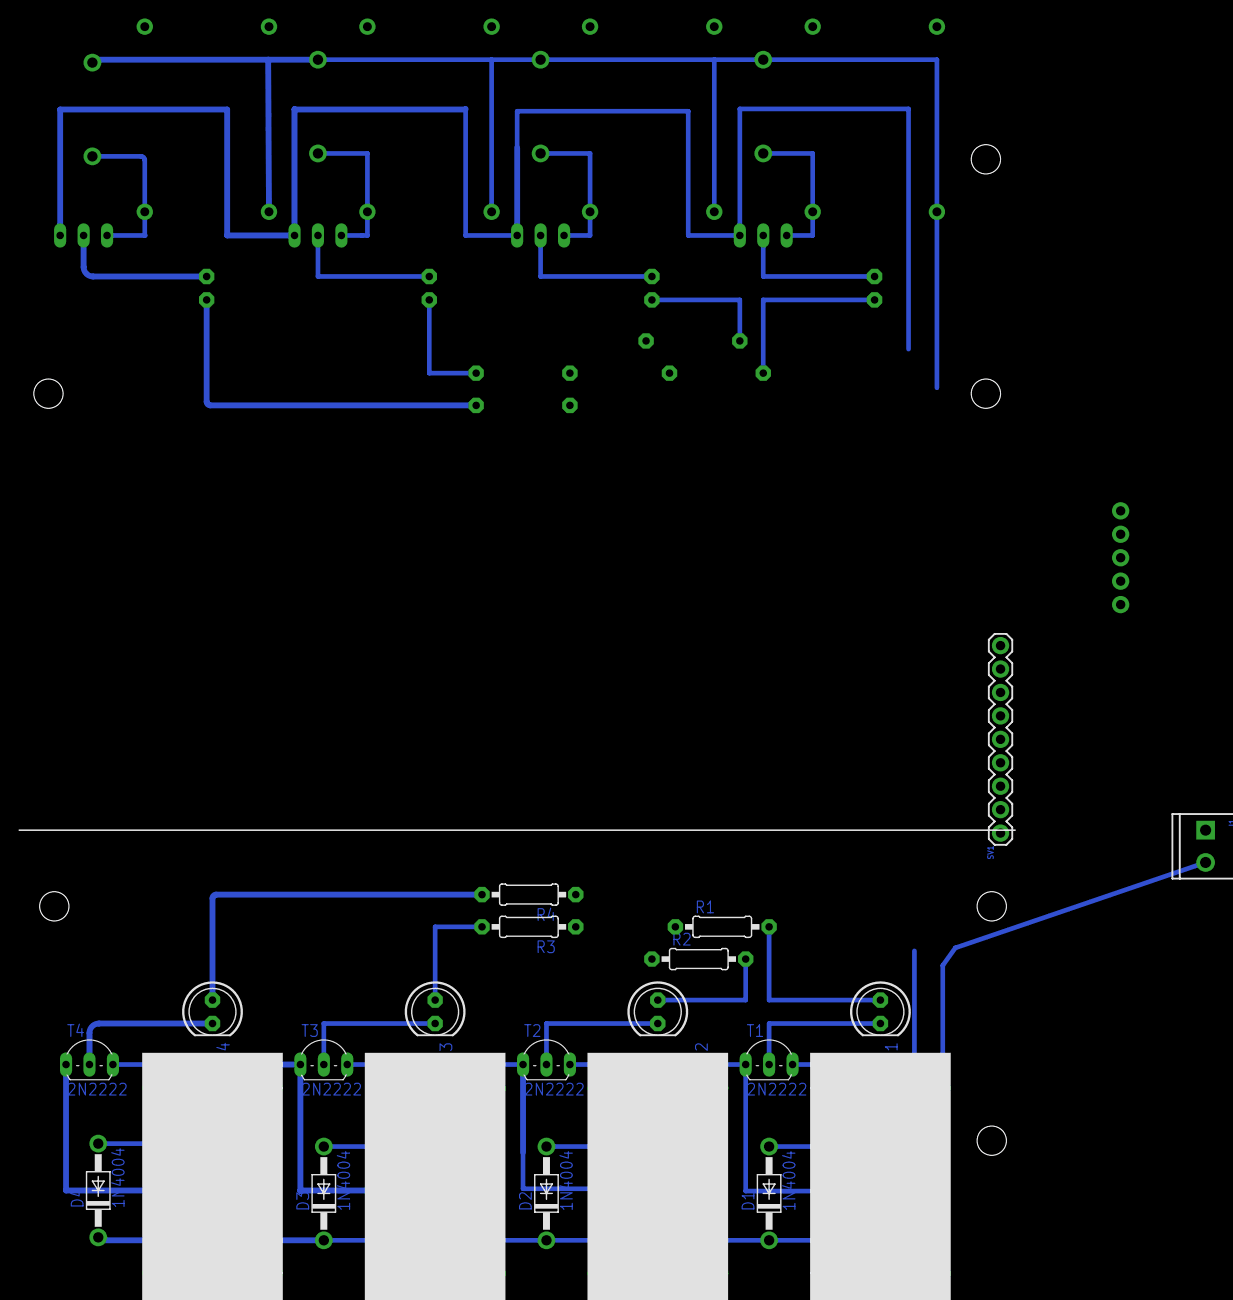
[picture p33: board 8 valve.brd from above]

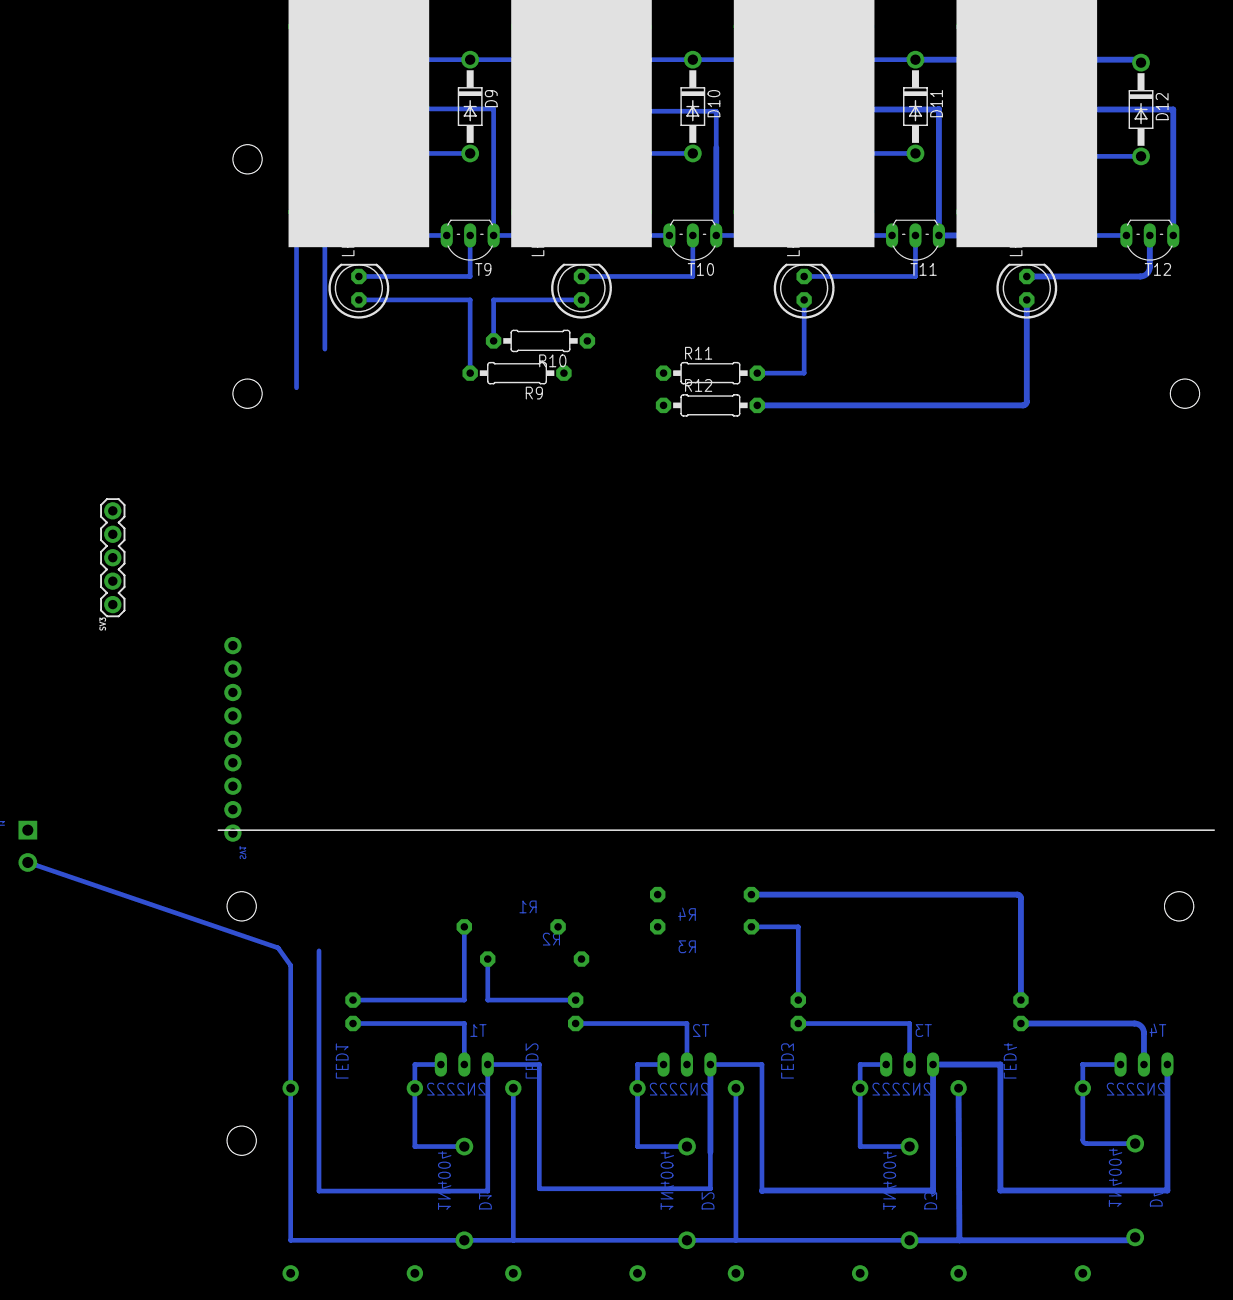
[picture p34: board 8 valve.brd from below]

Board: 2 copper layers, 43 parts (21 on the bottom side), 33 nets.

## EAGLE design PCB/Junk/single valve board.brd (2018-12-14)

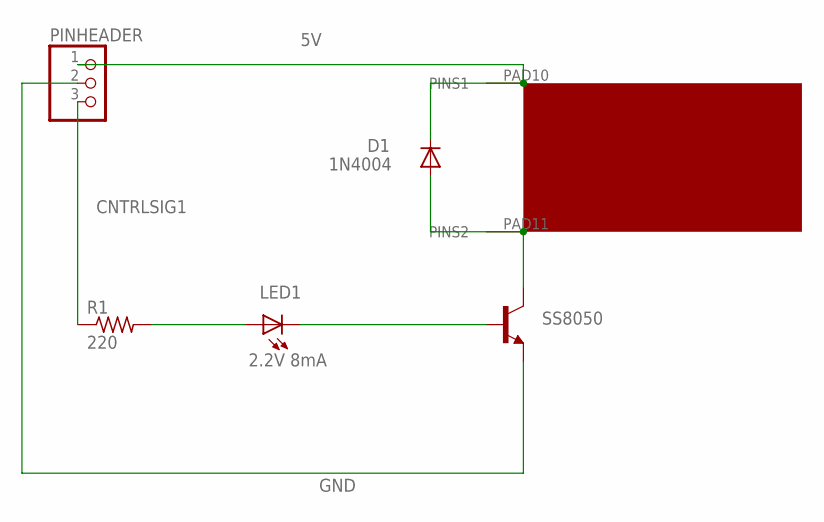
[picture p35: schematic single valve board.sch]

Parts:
D1: 1N4004; DO41-10
LED1: 2.2V 8mA; LED5MM
PINHEADER: PINHD-1X3; 1X03
R1: 220; 0207/10
SOLENOID1: SOLENOID1; VALVTEST2
SS8050: 2N2222; TO92-EBC-OVAL

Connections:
5V: D1.C, PINHEADER.1, SOLENOID1.PAD10 (PINS1)
CNTRLSIG1: PINHEADER.3, R1.1
GND: PINHEADER.2, SS8050.E
unnamed: D1.A, SOLENOID1.PAD11 (PINS2), SS8050.C
unnamed: LED1.K (C), SS8050.B
unnamed: LED1.A, R1.2

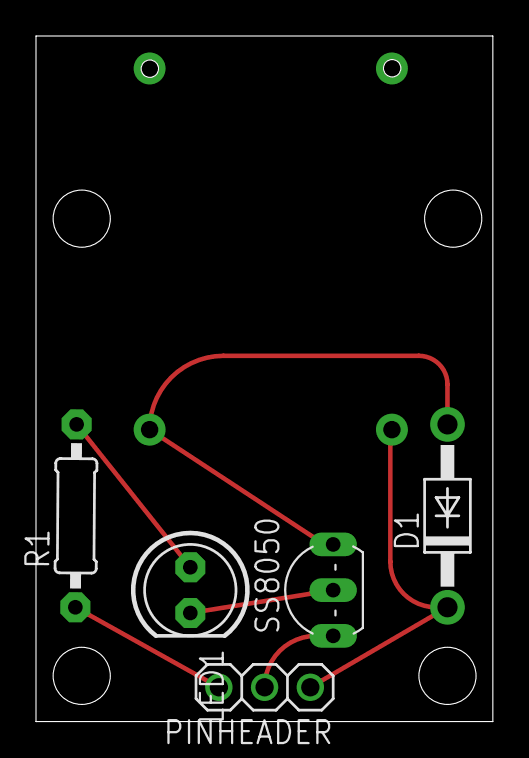
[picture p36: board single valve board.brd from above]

Board: 2 copper layers, 25.4 x 38.1 mm, 6 parts (1 on the bottom side), 6 nets.

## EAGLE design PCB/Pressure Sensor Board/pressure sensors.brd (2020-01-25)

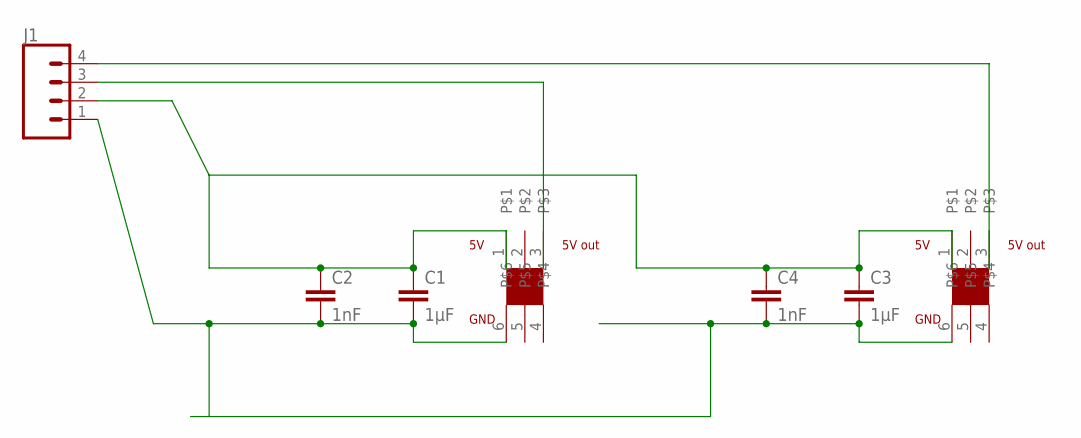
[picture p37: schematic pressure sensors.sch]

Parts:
C1, C3: 1µF; C050-030X075
C2, C4: 1nF; C050-030X075
J1: CONN_04; 1X04
U$1: 1; DIP750W53P254L720H850Q6B
U$2: ADP5101; DIP750W53P254L720H850Q6B

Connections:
5V: C1.1, C2.1, C3.1, C4.1, J1.2, U$1.1, U$2.1
GND: C1.2, C2.2, C3.2, C4.2, J1.1, U$1.6, U$2.6
unnamed: J1.3, U$1.3
unnamed: J1.4, U$2.3

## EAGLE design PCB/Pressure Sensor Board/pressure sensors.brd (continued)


Board: 2 copper layers, 31.8 x 25.4 mm, 7 parts (0 on the bottom side), 4 nets.

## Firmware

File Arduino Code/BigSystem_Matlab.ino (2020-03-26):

#include "Big_system.h"
//--pump control
//change these values to control how the pressure is controlled in the system.

// positive pressure control high/low values. Units are in KPa. Make sure High > Low


// Negative pressure control high/low values. Units are in KPa. Make sure High < Low, different than positive




//this is how hard the pumps work. 0= 0%, 255= 100% The pumps wont turn on if the value is too low.
int pumppower = 190;

//-----

float inputvalue;
float voltage;
float pressure;


void setup() {

  initializepins();
  Serial.begin(19200);
    int n_pres_sensor = analogRead(A14);
  int p_pres_sensor = analogRead(A15);
  int o_pres_sensor1 = analogRead(A13);
  int o_pres_sensor2=analogRead(A12);
  int o_pres_sensor3=analogRead(A11);
int o_pres_sensor4=analogRead(A10);
int o_pres_sensor5=analogRead(A9);

}

void loop() {

  pressurecontrol(n_pres_sensor, p_pres_sensor, o_pres_sensor1,o_pres_sensor2,o_pres_sensor3,o_pres_sensor4,o_pres_sensor5,pumppower);
  unsigned long currentMillis = millis(); 
 
  
  
  recvWithStartEndMarkers();
 
 if (newData == true) {
        strcpy(tempChars, receivedChars);
            // this temporary copy is necessary to protect the original data
            //   because strtok() used in parseData() replaces the commas with \0
        parseData();
        act_on_input();
        newData = false;
 }


}

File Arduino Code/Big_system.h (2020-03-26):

#define Big_system.h

#include "Arduino.h"
#define OPEN 1
#define CLOSE 0

//define output pins
const int invalve[3] = { 53, 52, 51};
//const int ovalve[8] = {28, 47, 29, 46,30,45,31,44}; //this pin arrangement is for the 8-channel device only
const int ovalve[8] = {47, 46, 45, 44, 31, 30, 29, 28};
const int pump[2] = {6, 5};
const int positivepumppin = 6;
const int negativepumppin = 5;

int pumpstatus[2] = {0, 0};
int invalvestatus[3];
int ovalvestatus[8];
int nsetpoint = 0;
int psetpoint = 0;
float p_pressure;
float n_pressure;
float o1_pressure;
float o2_pressure;
float o3_pressure;
float o4_pressure;
float o5_pressure;
float p_pressure_avg = 0;
float n_pressure_avg = 0;
float o1_pressure_avg = 0;
float o2_pressure_avg = 0;
float o3_pressure_avg = 0;
float o4_pressure_avg = 0;
float o5_pressure_avg = 0;
int dly = 25;
bool p_switch;
int pin;
int incomingByte;
unsigned long calltime;

const int numReadings = 30;

int readings[numReadings];      // the readings from the analog input
int readIndex = 0;              // the index of the current reading
int total = 0;                  // the running total
int average = 0;
bool wait;

const byte numChars = 32;
char receivedChars[numChars];
char tempChars[numChars];
char messageFromPC[numChars] = {0};
int integerFromPC = 0;
float floatFromPC = 0.0;
boolean newData = false;


char invalve_read[] = "VI";
char ovalve_read[] = "VO";
char psp[] = "PSP";
char nsp[] = "NSP";
char pvp[] = "PVP";
char pvn[] = "PVN";
char pvo[] = "PVO";
char aov[] = "AOV";
char aiv[] = "AIV";
char pvt[] = "PVT";

//----ARDUINO INITIALIZATION
void initializepins() {
  for (int i = 0; i < 3; i++) {
    pinMode(invalve[i], OUTPUT);
    digitalWrite(invalve[i], LOW);
  }

  for (int i = 0; i < 8; i++) {
    pinMode(ovalve[i], OUTPUT);
    digitalWrite(ovalve[i], LOW);

  }

}
//---------------

//---THIS FUNCTION TURNS ON/OFF ALL INPUT VALVES
void setallinvalves(int position) {
  if (position == OPEN) {
    for (int i = 0; i < 3; i++) {
      digitalWrite(invalve[i], HIGH);
    }
  }

  if (position == CLOSE) {
    for (int i = 0; i < 3; i++) {
      digitalWrite(invalve[i], LOW);
    }
  }

}

//---------------------


//---THIS FUNCTION TURNS ON/OFF A SPECIFIC INPUT VALVE
void setinvalve(int number, int position) {
  if (position == OPEN) {
    digitalWrite(invalve[number], HIGH);

  }

  if (position == CLOSE) {
    digitalWrite(invalve[number], LOW);
  }
}
//---------------


//---THIS FUNCTION TURNS ON/OFF ALL OUTPUT VALVES
void setalloutvalves(int position) {
  if (position == OPEN) {
    for (int i = 0; i < 8; i++) {
      digitalWrite(ovalve[i], HIGH);
    }
  }

  if (position == CLOSE) {
    for (int i = 0; i < 8; i++) {
      digitalWrite(ovalve[i], LOW);
    }
  }
}

//----------------------------

//---THIS FUNCTION TURNS ON/OFF A SPECIFIC OUTPUT VALVE
void setoutvalve(int number, int position) {
  if (position == OPEN) {
    digitalWrite(ovalve[number], HIGH);
  }
  if (position == CLOSE) {
    digitalWrite(ovalve[number], LOW);
  }
}
//-------


void pressurecontrol(int n_input, int p_input, int o1_input, int o2_input, int o3_input, int o4_input, int o5_input, int power) {

  //sensor math to convert input voltage to pressure in KPa
  float  o1_voltage = map(o1_input, 0, 1023, 0, 5000);
  float  o2_voltage = map(o2_input, 0, 1023, 0, 5000);
  float  o3_voltage = map(o3_input, 0, 1023, 0, 5000);
  float  o4_voltage = map(o4_input, 0, 1023, 0, 5000);
  float  o5_voltage = map(o5_input, 0, 1023, 0, 5000);
  float  n_voltage = map(n_input, 0, 1023, 0, 5000);
  float  p_voltage = map(p_input, 0, 1023, 0, 5000);

  n_pressure = 50 * (n_voltage / 1000) - 125.1;
  p_pressure = 50 * (p_voltage / 1000) - 124.85;
  o1_pressure = 50 * (o1_voltage / 1000) - 124.6;
  o2_pressure = 50 * (o2_voltage / 1000) - 125.35;
  o3_pressure = 50 * (o3_voltage / 1000) - 124.1;
  o4_pressure = 50 * (o4_voltage / 1000) - 124.85;
  o5_pressure = 50 * (o5_voltage / 1000) - 125.35;

  for (int i = 0; i < 99; i++) {
    p_pressure_avg = p_pressure_avg + p_pressure;
    n_pressure_avg = n_pressure_avg + n_pressure;
    o1_pressure_avg = o1_pressure_avg + o1_pressure;
    o2_pressure_avg = o2_pressure_avg + o2_pressure;
    o3_pressure_avg = o3_pressure_avg + o3_pressure;
    o4_pressure_avg = o4_pressure_avg + o4_pressure;
    o5_pressure_avg = o5_pressure_avg + o5_pressure;
  }

  p_pressure_avg = p_pressure_avg / 100;
  n_pressure_avg = n_pressure_avg / 100;
  o1_pressure_avg = o1_pressure_avg / 100;
  o2_pressure_avg = o2_pressure_avg / 100;
  o3_pressure_avg = o3_pressure_avg / 100;
  o4_pressure_avg = o4_pressure_avg / 100;
  o5_pressure_avg = o5_pressure_avg / 100;


  // Serial.print("Positive Pressure is: ");
  // Serial.print(p_pressure_avg);
  // Serial.print(", Negative Pressure is: ");
  // Serial.println(n_pressure_avg);
  // Serial.println(",");
  //Serial.print("Output Pressures: ");
  //Serial.print(o1_pressure_avg);
  //Serial.print(", ");
  //Serial.print(o2_pressure_avg);
  //Serial.print(", ");
  //Serial.print(o3_pressure_avg);
  //Serial.print(", ");
  //Serial.print(o4_pressure_avg);
  //Serial.print(", ");
  //Serial.println(o5_pressure_avg);

  //pressure regulation
  if (p_pressure_avg < (psetpoint - .3)) {
    analogWrite(positivepumppin, power);

  }

  if (abs(p_pressure_avg) > psetpoint) {

    analogWrite(positivepumppin, 0);
  }

  if (n_pressure_avg > (nsetpoint + .3)) {
    analogWrite(negativepumppin, power);

  }
  if (n_pressure_avg < nsetpoint) {

    analogWrite(negativepumppin, 0);
  }


}
//-----------------------

//---THIS FUNCTION SWITCHES PRESSURE USING A QUICK NEUTRAL PRESSURE EVACUATION FIRST
void pressure_switch(int pin, int current, int when) {
  setinvalve(2, OPEN);
  if ((unsigned long)(current - when) >= dly) {
    p_switch = false;
    setinvalve(2, CLOSE);
    setinvalve(pin, OPEN);
  }
}

//---THIS SECTION PULLS OUT VALUES FROM A SERIAL INPUT SO IT CAN BE READ AND EXECUTED ON
void parseData() {      // split the data into its parts

  char * strtokIndx; // this is used by strtok() as an index

  strtokIndx = strtok(tempChars, ",");     // get the first part - the string
  strcpy(messageFromPC, strtokIndx); // copy it to messageFromPC

  strtokIndx = strtok(NULL, ","); // this continues where the previous call left off
  integerFromPC = atoi(strtokIndx);     // convert this part to an integer

  strtokIndx = strtok(NULL, ",");
  floatFromPC = atof(strtokIndx);     // convert this part to a float

}

// This section is looking for new serial inputs and parsing them
void recvWithStartEndMarkers() {
  static boolean recvInProgress = false;
  static byte ndx = 0;
  char startMarker = '<';
  char endMarker = '>';
  char rc;

  while (Serial.available() > 0 && newData == false) {
    rc = Serial.read();

    if (recvInProgress == true) {
      if (rc != endMarker) {
        receivedChars[ndx] = rc;
        ndx++;
        if (ndx >= numChars) {
          ndx = numChars - 1;
        }
      }
      else {
        receivedChars[ndx] = '\0'; // terminate the string
        recvInProgress = false;
        ndx = 0;
        newData = true;
      }
    }

    else if (rc == startMarker) {
      recvInProgress = true;
    }
  }
}
//============ This section acts 
void act_on_input() {
  if (strcmp(messageFromPC, invalve_read) == 0) {
    setinvalve(integerFromPC, floatFromPC);
  }
  if (strcmp(messageFromPC, ovalve_read) == 0) {
    setoutvalve(integerFromPC, floatFromPC);
  }
  if (strcmp(messageFromPC, nsp) == 0) {
    nsetpoint = integerFromPC;
  }
  if (strcmp(messageFromPC, psp) == 0) {
    psetpoint = integerFromPC;
  }
  if (strcmp(messageFromPC, pvp) == 0) {
    Serial.println(p_pressure_avg);
  }
  if (strcmp(messageFromPC, pvn) == 0) {
    Serial.println(n_pressure_avg);
  }

  if (strcmp(messageFromPC, pvo) == 0) {
    if (integerFromPC == 1) {
      Serial.println(o1_pressure_avg);
    }
    if (integerFromPC == 2) {
      Serial.println(o2_pressure_avg);
    }
    if (integerFromPC == 3) {
      Serial.println(o3_pressure_avg);
    }
    if (integerFromPC == 4) {
      Serial.println(o4_pressure_avg);
    }
    if (integerFromPC == 5) {
      Serial.println(o5_pressure_avg);
    }
  }
  if (strcmp(messageFromPC, pvt) == 0) {
    Serial.println(o2_pressure_avg);
  }
  if (strcmp(messageFromPC, aov) == 0) {
    setalloutvalves(integerFromPC);
  }
  if (strcmp(messageFromPC, aiv) == 0) {
    setallinvalves(integerFromPC);
  }
}

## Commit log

2018-12-08 initialization of the project
    [12v pump.f3d, ArduinoMega v1.f3d, L298N v1.f3d, air tank v1.f3d]
2018-12-10 pcb boards and cad
    [IO Valve testing.brd, IO Valve testing.sch, IO Valve.brd, IO Valve.sch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]
2018-12-10 update board
    [single valve board.brd, single valve board.sch]
2018-12-10 board update
    [single valve board.brd]
2018-12-14 pressure sensor board update
    [single valve board.brd, single valve board.sch]
2018-12-15 board updates
    [3 valve front connect.brd, 3 valve front connect.sch, 3 valve.brd, 3 valve.sch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]
2018-12-15 update psensor
    [pressure sensors.brd]
2018-12-15 increased hole size for pressure sensor
    [pressure sensors.brd, pressure sensors.sch]
2018-12-15 sensors agin
    [pressure sensors.brd, pressure sensors.sch]
2018-12-16 4 valve boards
    [4 board.brd, 4 board.sch, 4 valve front connect.brd, 4 valve front connect.sch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]
2019-01-18 mini system board
    [4 valve front connect.brd, mini system.brd, mini system.sch]
2019-01-18 new board
    [mini system.brd]
2019-01-27 new mini system
    [mini system- 5 components vertical moved nano.brd, mini system- 5 components vertical moved nano.sch, mini system- 5 components vertical.brd, mini system- 5 co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]
2019-05-16 added new arduino code and matlab scripts
2019-05-27 test data May 27
    [05-17-2019-1433-test0-0.csv, 05-17-2019-1434-test0-1.csv, 05-17-2019-1434-test0-2.csv, 05-17-2019-1434-test1-0.csv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]
2019-07-03 new stuff
    [06-10-2019-1255-GKtest-1-339-1.csv, 06-10-2019-1256-GKtest-1-339-2.csv, 06-10-2019-1258-GKtest-1-339-3.csv, 06-10-2019-1259-GKtest-1-339-4.csv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]
2019-07-03 new data
    [07-03-2019-1303-RG_pressure_test0-1.csv, 07-03-2019-1304-RG_pressure_test0-2.csv, 07-03-2019-1304-RG_pressure_test0-3.csv, 07-03-2019-1305-RG_pressure_test0-4.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]
2019-09-09 add contact swithcing
    [08-14-2019-1832-GKtest-neutral-2-0-1.csv, 08-14-2019-1836-GKtest-neutral-2-0-1.csv, 08-14-2019-1839-GKtest-neutral-2-0-1.csv, 08-14-2019-1843-GKtest-neutral-2-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]
2020-01-21 updated BOM
    [06-05-2019-1155-RGtest339-1.csv, 06-05-2019-1157-RGtest339-2.csv, 06-05-2019-1159-RGtest339-3.csv, 06-05-2019-1201-RGtest339-1.csv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]
2020-01-21 moved BOM to components
    [BOM Big Pneumatics.xlsx]
2020-01-24 update arduino code and add matlab program
    [08-14-2019-1832-GKtest-neutral-2-0-1.csv]
2020-01-24 update arduino code
2020-01-24 Created Arduino Serial Command List
2020-01-25 Update Arduino Command List
2020-01-25 Added Images of PCBs and sorted
    [3 valve front connect.brd, 3 valve front connect.sch, 3 valve.brd, 3 valve.sch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]
2021-02-08 Fixed labeling of 5V and GND inputs

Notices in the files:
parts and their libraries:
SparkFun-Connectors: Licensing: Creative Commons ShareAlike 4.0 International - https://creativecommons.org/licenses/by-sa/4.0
